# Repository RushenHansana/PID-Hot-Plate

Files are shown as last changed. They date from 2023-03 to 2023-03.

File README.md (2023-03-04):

# PID-Hot-Plate
This is the PID Hot Plate project we developed as the project for our Laboratory Practice module.
The contributors involved are Rushen Dissanayaka, Pabadhi Liyanage, Sithija Vihanga  and Oshan Yalegama.
The PCB designs and circuit schematics were created using Altium Designer.
The enclosure design was completed using Solidworks.

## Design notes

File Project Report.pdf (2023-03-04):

## University of Moratuwa Faculty of Engineering Department of Electronic & Telecommunication Engineering

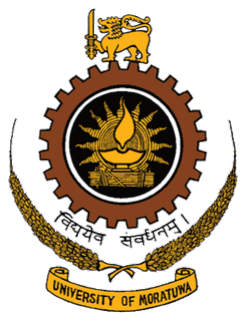
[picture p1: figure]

# Hot-plate Controller using PID

## Group Members(Group No. 24)

Index No. | Name
200134R 200352H 200506K 200740V | Disanayaka R.M.R.H. Liyanage P.H.S. Ranaraja S.V. Yalegama M.M.O.A.B.

## Submission Date: February 27, 2023

## This report is submitted as a partial fulfilment of module EN2091

## Contents

1 Introduction | 2
2 Functionality | 2
2.1 Sensor interfacing unit | | 2
2.2 PID controller unit | | 2
2.3 Firing Angle Unit | | 3
2.4 Power Supply Unit | | 3
2.5 Functional block diagram | | 4
3 System model with design parameters | 4
3.1 Sensor interfacing unit | | 4
3.2 PID controller unit | | 4
3.3 Firing angle unit | | 5
3.4 Power supply unit | | 5
4 Schematic | 5
4.1 Sensor interfacing unit | | 5
4.2 PID controller unit | | 5
4.3 Firing angle unit | | 5
4.4 Power supply unit | | 6
5 Simulation results | 6
5.1 PID controller unit | | 6
5.2 Sensor interfacing unit | | 6
5.3 Firing angle unit | | 6
5.4 PWM signal generation | | 7
5.5 Output | | 7
6 PCB design | 7
6.1 Sensor interfacing unit | | 7
6.2 PID controller unit | | 7
6.3 Firing angle unit | | 8
6.4 Power supply unit | | 8
7 Enclosure Design | 8
8 Individual contribution of each group member | 9
9 Conclusion and future works | 9

## Abstract

The objective of this project is to implement a hot plate controller using a PID controller unit. Here, we have used totally analog electronics-based concepts and a PID controller to keep temperature at a desired level. The implemented hot plate can be heated up to 200 ◦C. The PID controller takes the difference between the input temperature and the sensed temperature as the error signal, and then gives the sum of the proportional, derivative, and integral signals to the error signal as the output. Then, the firing angle controller unit controls the power by using PID output and keeps the temperature of the hotplate at the desired level.

## 1 Introduction

This is an analog electronics-based project. The primary concept which we have followed in this project is controlling the temperature of the hotplate by using a PID control unit. For the sake of ease and proper organization, the project has been divided into four main subtasks. The PID controller unit, sensor interfacing unit, firing angle, and power supply unit The difference between user input and sensor output is fed to the PID as an error signal. The PID controller generates proportional, derivative, and integral signals from the error signal. The firing angle unit generates a PWM signal according to the PID output to control the firing angle. Finally, from the power supply unit, a plate will be heated to the desired level. A specially designed hot plate can be heated up to 200 ◦C. As the hot plate’s input power supply, a 230-volt domestic power supply should be provided.

## 2 Functionality

### 2.1 Sensor interfacing unit

Measuring the current temperature of the coil is essential in order to control the temperature of the coil. Therefore, a temperature sensor is used to measure the current temperature. The sensor interface unit also takes the set temperature from the user as an input. It subtracts the voltage, which is calibrated according to the set temperature and the sensor output. Then, it generates the error signal. This error signal feeds the PID controller unit.

### 2.2 PID controller unit

PID is a feedback-based control strategy that adjusts the system’s output based on the difference between the desired setpoint and the actual variable. Instrument Society of America[1].The proportional term provides an output signal that is proportional to the error signal that is given by the sensor interface unit. The integral term sums up the error over time and produces an output to reduce any steady-state error. This aids in reaching the hot plate at the precise temperature set by the user. The derivative term measures the rate of change of the error and produces a control output to decrease overshoot. With the optimal combination of these three terms, we can reduce the time taken to reach the set temperature and maintain it exactly at the required level.
The proportionality constant is represented by the letter ”Kp” and determines the proportion of the error signal that is applied to the control output. Increasing Kp will increase the responsiveness of the system. However, it can also lead to overshoot and instability.
The integral constant, represented by the letter ”Ki,” determines the amount of past error that is summed up and used to adjust the control output. This term involves reducing steady-state error. But it can also lead to instability if the value of ”Ki” is too high.
The derivative constant, represented by the letter ”Kd,” determines the rate at which the error is changing over time and uses this information to adjust the control output. This term helps to reduce overshoot. The optimal values of these constants are achieved by a process called tuning.
The sum of proportional, integral, and derivative signals will be fed to the firing angle unit

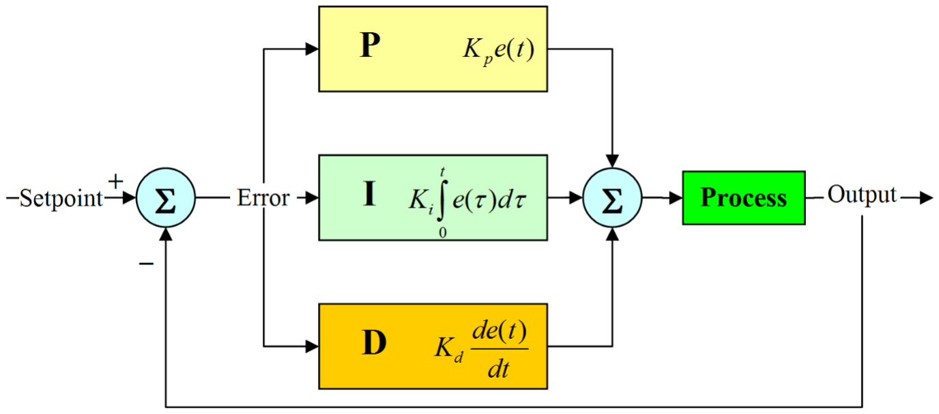
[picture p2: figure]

Figure 1: functionality diagram of a PID controller

### 2.3 Firing Angle Unit

Introduction

The firing angle unit controls the amount of power supplied to the coil based on PID output. Zero crossing detection, ramp generation, PWM signal generation, and the TRIAC control circuit are the main subunits of the firing angle unit.

1. Detection of Zero Crossings
In order to detect zero-crossings, each halfcycle of the AC waveform is given an equal pulse. This enables control of every halfcycle of the AC waveform in the same way. When the voltage of the rectified AC waveform is lower than 0.7V, the output of the zero-crossing detector is 12V; it is zero otherwise.

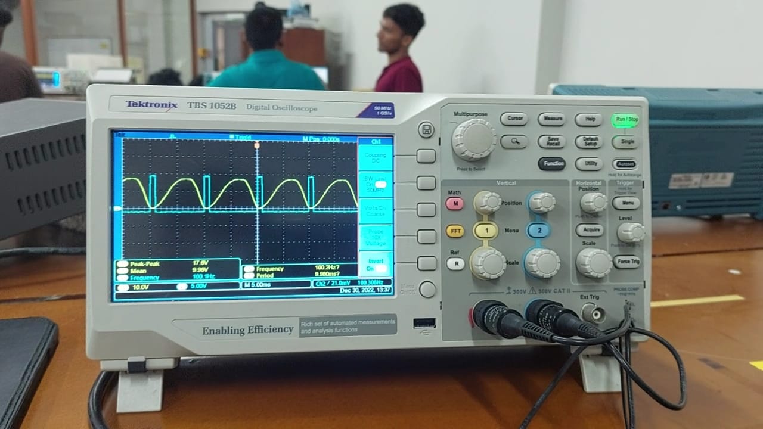
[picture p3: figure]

2. Ramp Generation
The ramp is generated by charging and discharging a capacitor. When the output of the zero-crossing detector is less than the threshold voltage of the transistor, the capacitor will be charged. When the output of the zero-crossing detector is high, the transistor will be saturated and the capacitor will be discharged. The ramp works as a threshold for PWM signal generation.

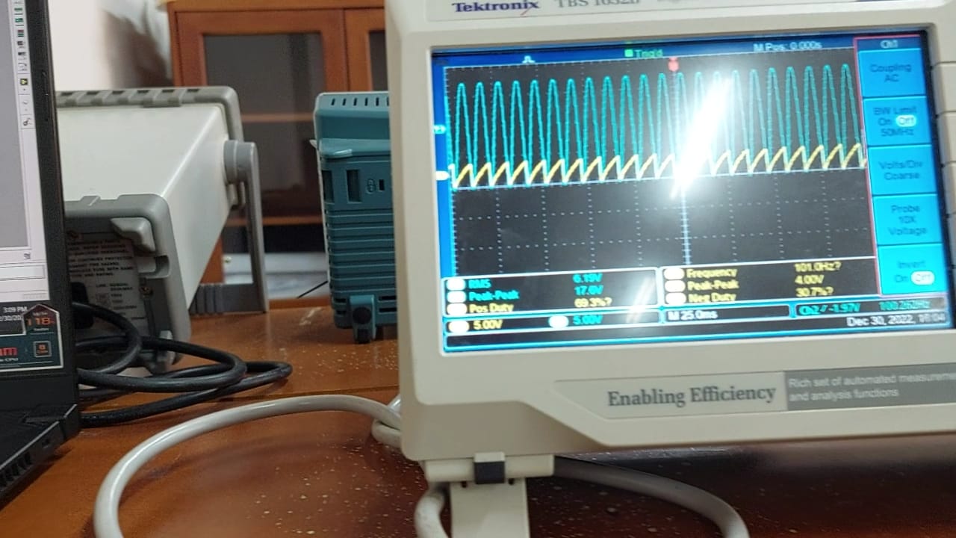
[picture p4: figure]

3. PWM signal generation
The main task of this subunit is to create a PWM signal, which is used to control the AC power. When the ramp voltage is lower than the PID output voltage, the output of the subunit is 0V and otherwise, it is 12V. The width of the pulse gradually decreases when the output voltage of the PID increases. Conversely, pulse width increases when the output of the PID drops.

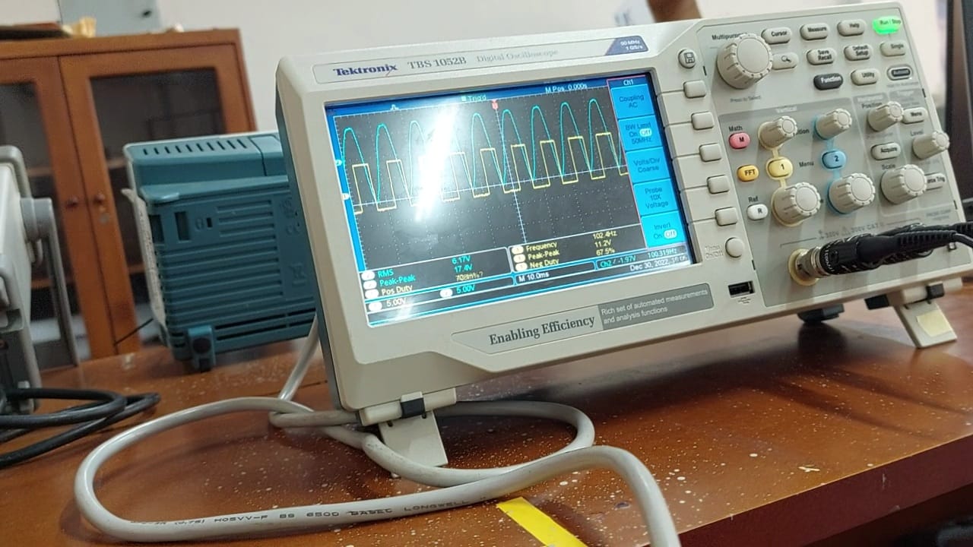
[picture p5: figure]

4. TRIAC Control Circuit
The PWM signal is passed to the optocoupler through a transistor. The optocoupler creates electrical isolation between the lowand high-voltage circuits. The TRIAC, which is connected to the optocoupler, acts as a switch to the AC source. The optocoupler’s output signal, which is connected to the TRIAC, controls the AC waveform.

### 2.4 Power Supply Unit

The hotplate draws power from the domestic power supply (230 V, 50 Hz). But the sensors, opamps, and most of the other components use low voltage to function. For instance, op-amps function at -12V and 12V. The function of the power supply unit is to supply the required voltages to relevant components.

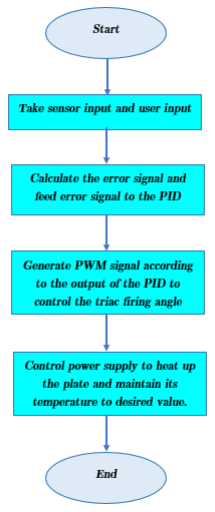
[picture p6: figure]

### 2.5 Functional block diagram

## 3 System model with design parameters

### 3.1 Sensor interfacing unit

There are several options available in sensing the temperature of the hot plate. When deciding a sensor to be used, the requirements that should be fulfilled by the sensor are, a linear relationship between voltage and temperature, compactness, high operating temperature, availability in the market, quick response time and simplicity in signal processing. One of the available options is a thermocouple but it is not suitable for our project due to the need for a reference temperature and the complexity of the signal processing required. We decided to use a PT100 which is an RTD (Resistance Temperature Detector). The sensor has an operating temperature of up to 800C and has a resistance that varies with temperature. The sensor interface produces an output voltage corresponding to the resistance of the sensor by the

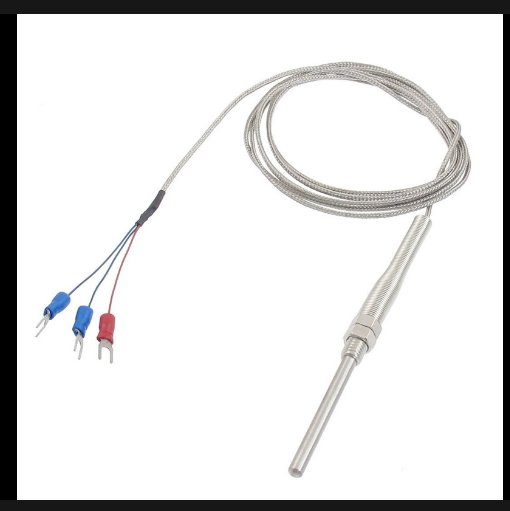
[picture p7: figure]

use of a constant current built from a BJT and amplifies and calibrates the result. The resulting voltage is then passed through a subtractor which calculates the error signal between this voltage and the voltage corresponding to the temperature set by the user. The resulting error signal is passed to the PID.
UA741 Op-amps were used throughout the interface as they perform well as voltage followers.
(a) PT100 sensor

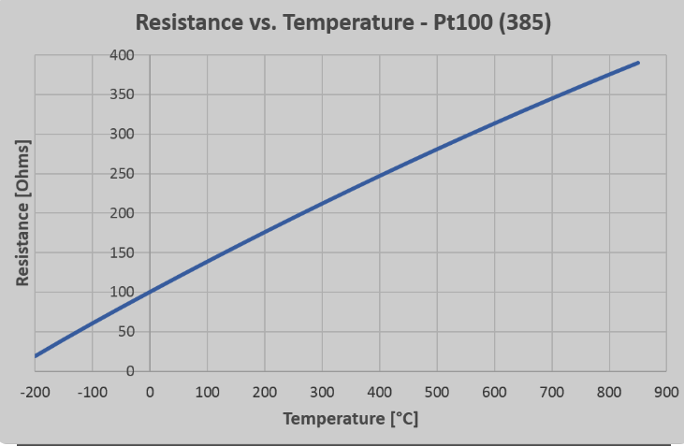
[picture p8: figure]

(b) Relationship between resistance vs temperature

Figure 2: For 100 kHz

Required temperature (input temperature by the user) and the current temperature are displayed by the OLED display.

### 3.2 PID controller unit

PID controller unit consist with an inverting amplifier, integrator circuit, subtractor circuit and a scaling adder. UA741CP op-amps are used to build those circuits due to its high gain, low input bias current, low input offset voltage and low cost. In each inverting amplifier, subtractor and integrator circuits, a pre-set is used as a feedback resistor and by changing the resistor value of the three pre-sets, Kp, Ki and Kd values can be changed.

### 3.3 Firing angle unit

We’re using LM324n op-amps for the triac firing angle circuit because they have enough slew rate to charge and discharge the 50V, 10uF capacitor with the generated impulse function (which is generated by comparing the full wave rectified 30V signal with 0.7V of the diode). For all the op-amps, we have used 12V and 0V as the power supply because we need to get a PWM signal as a positive output. For calibration purposes, two pre-sets have been added to user input voltage and to control the PWM signal amplitude. Because of that, a triac circuit can be independent from other input and output circuits. To handle both the 12V DC supply and the high-power supply for the load, we are using the optocoupler MOC3021, which can function up to 400V high power voltage. Moreover, triac BT137 has been used to slice the output AC supply voltage with respect to the input PWM signal to the optocoupler. On the high-power side, the triac can operate at up to 600 volts.

### 3.4 Power supply unit

The power supply unit consists of a center-tapped transformer, a rectifier bridge, capacitors, and voltage regulators. A center-tapped transformer converts domestic voltage into 12 volts. To obtain full wave rectification of the AC signal, a rectifier bridge is used. Unnecessary noises are avoided by the capacitors.

## 4 Schematic

### 4.1 Sensor interfacing unit

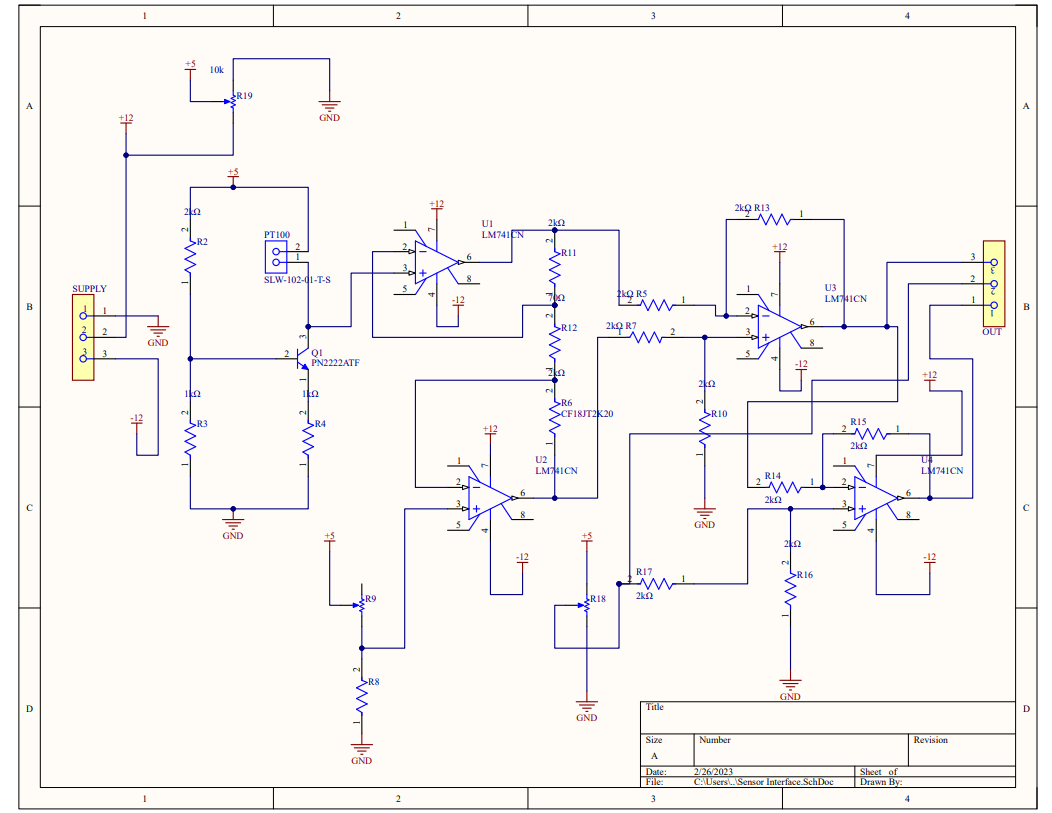
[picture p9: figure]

### 4.2 PID controller unit

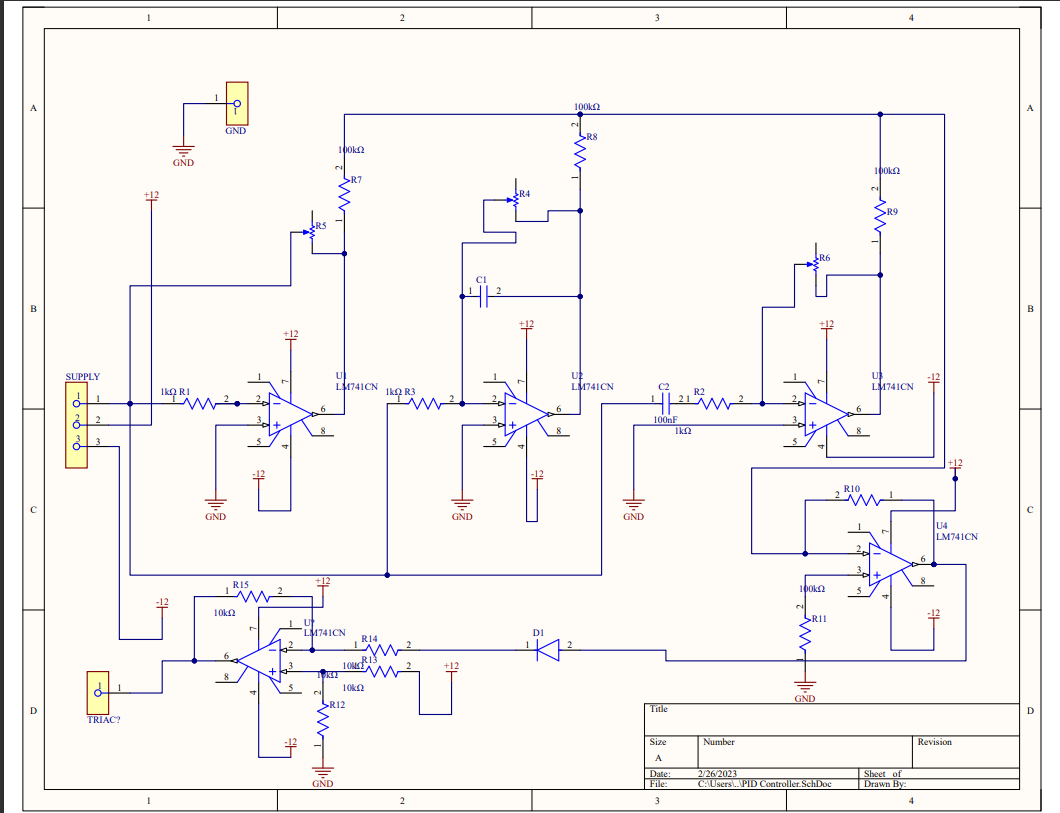
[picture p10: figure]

### 4.3 Firing angle unit

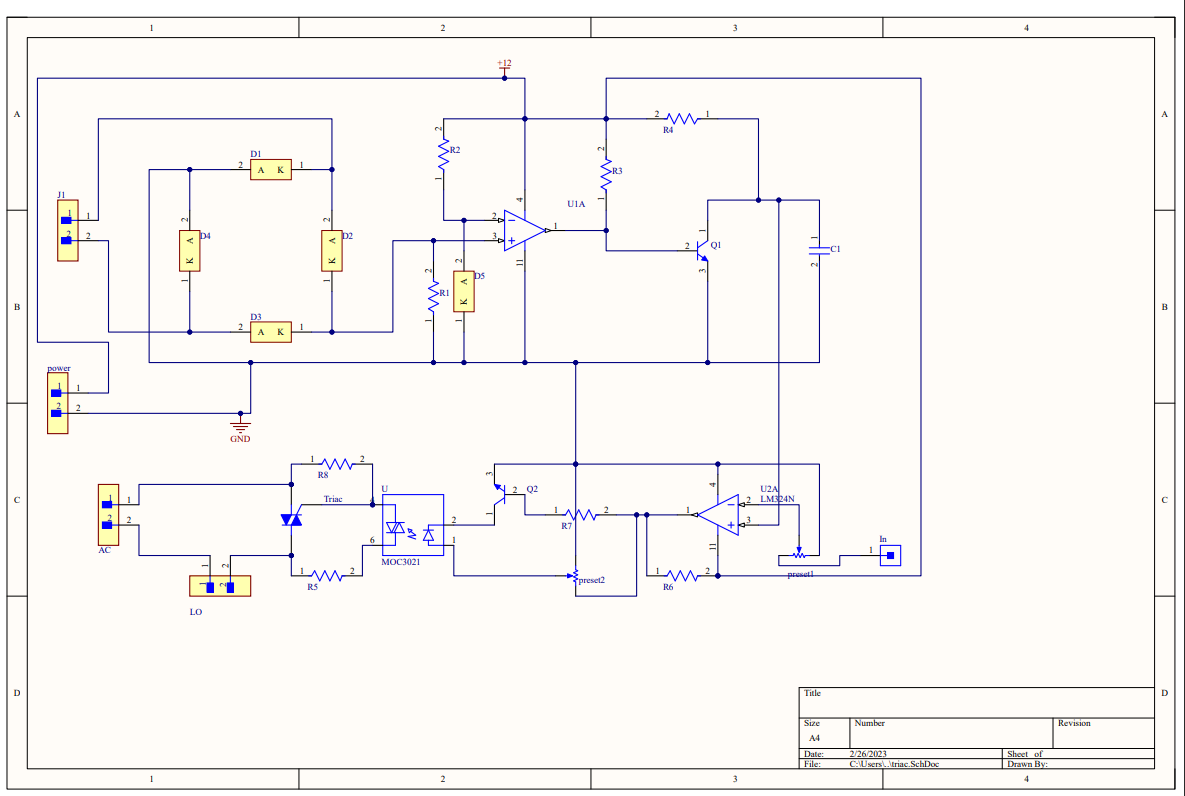
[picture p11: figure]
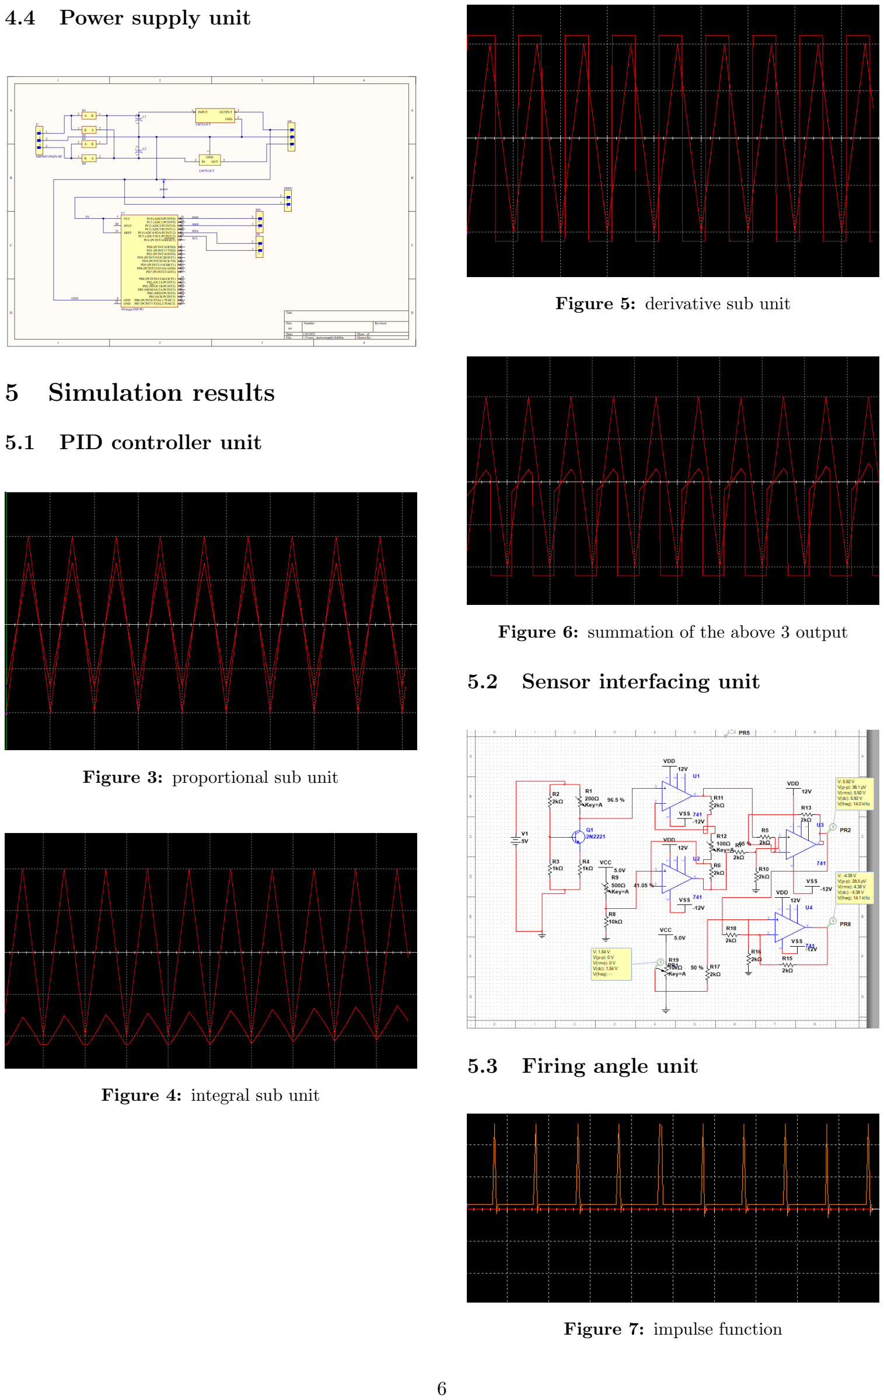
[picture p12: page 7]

### 4.4 Power supply unit

## 5 Simulation results

### 5.1 PID controller unit

Figure 3: proportional sub unit

Figure 4: integral sub unit

Figure 5: derivative sub unit

Figure 6: summation of the above 3 output

### 5.2 Sensor interfacing unit

### 5.3 Firing angle unit

Figure 7: impulse function

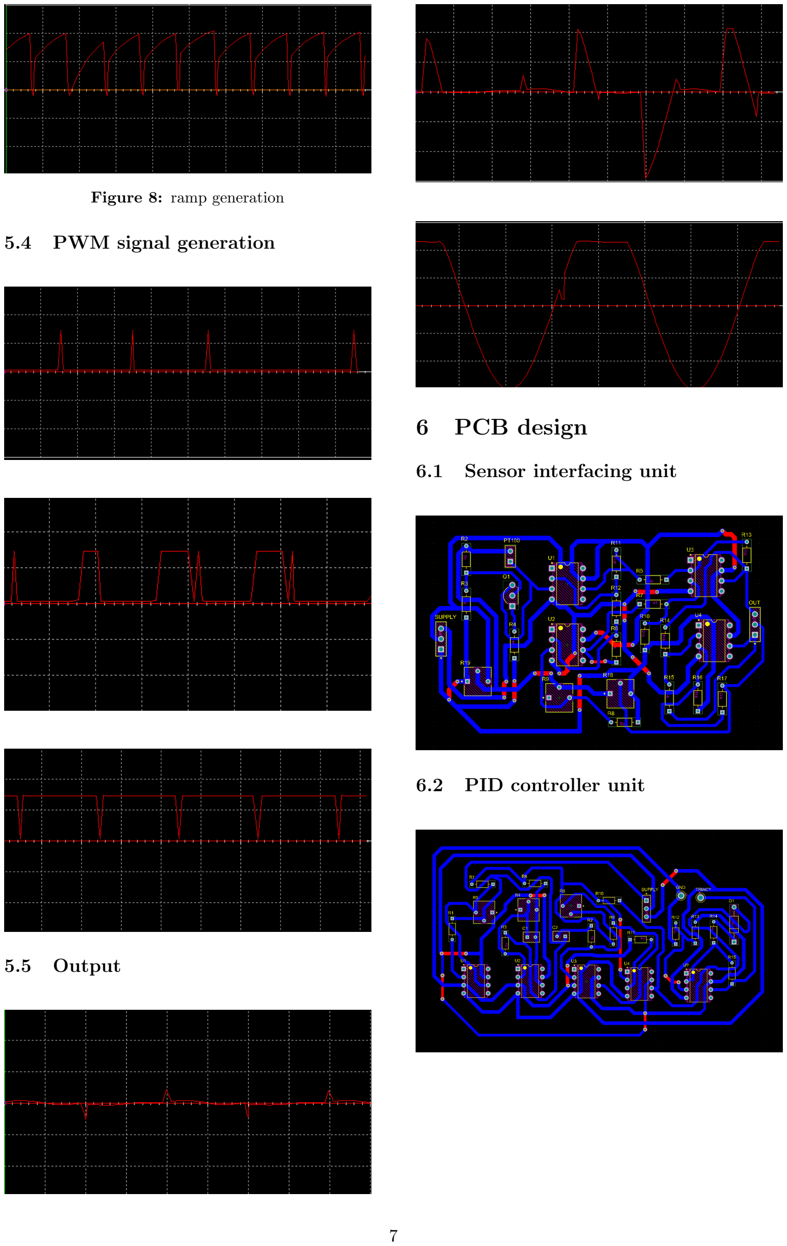
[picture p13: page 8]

Figure 8: ramp generation

### 5.4 PWM signal generation

### 5.5 Output

## 6 PCB design

### 6.1 Sensor interfacing unit

### 6.2 PID controller unit

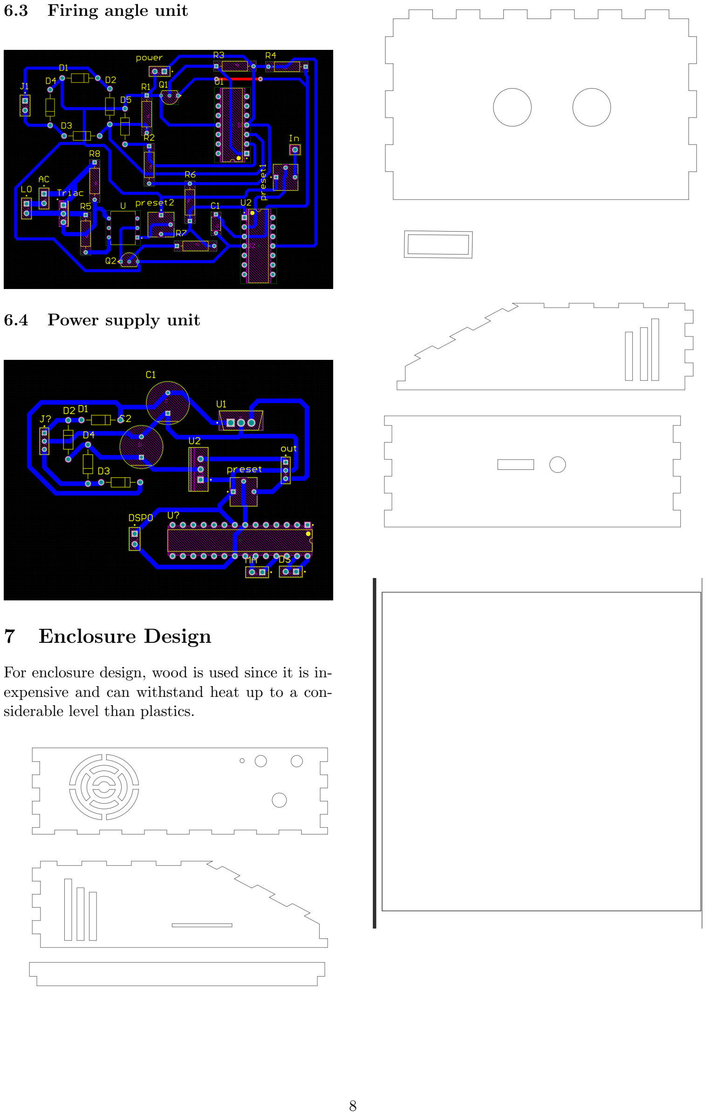
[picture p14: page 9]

### 6.3 Firing angle unit

### 6.4 Power supply unit

## 7 Enclosure Design

For enclosure design, wood is used since it is inexpensive and can withstand heat up to a considerable level than plastics.

## 8 Individual contribution of each group member

Group Members

Name. | Contribution
Disanayaka R.M.R.H. (200134R) | Power supply unit design
Liyanage P.H.S. (200352H) | PID control unit design
Ranaraja S.V. (200506K) | Firing angle unit design
Yalegama M.M.O.A.B. (200740V) | Sensor interfacing unit design

## 9 Conclusion and future works

In conclusion, the hot plate has been implemented by interconnecting four sub units which are sensor interfacing unit, PID controller unit, Firing angle unit and the power supply unit. The hotplate can be heated up to 200 ◦C. Also, the user can easily get the required information that he needs from the OLED display.
We are hoping to improve our hotplate design further in future. For that, we expect to tune the PID controller circuit precisely to get the optimal Kp, Ki and Kd values.
From those optimal values, we can heat up the coil up to desired temperature more quickly and maintain the hotplate temperature exactly at the desired temperature./

## References

[1] Karl J Astrom. “PID controllers: theory, design, and tuning”. In: The International Society of Measurement and Control (1995).

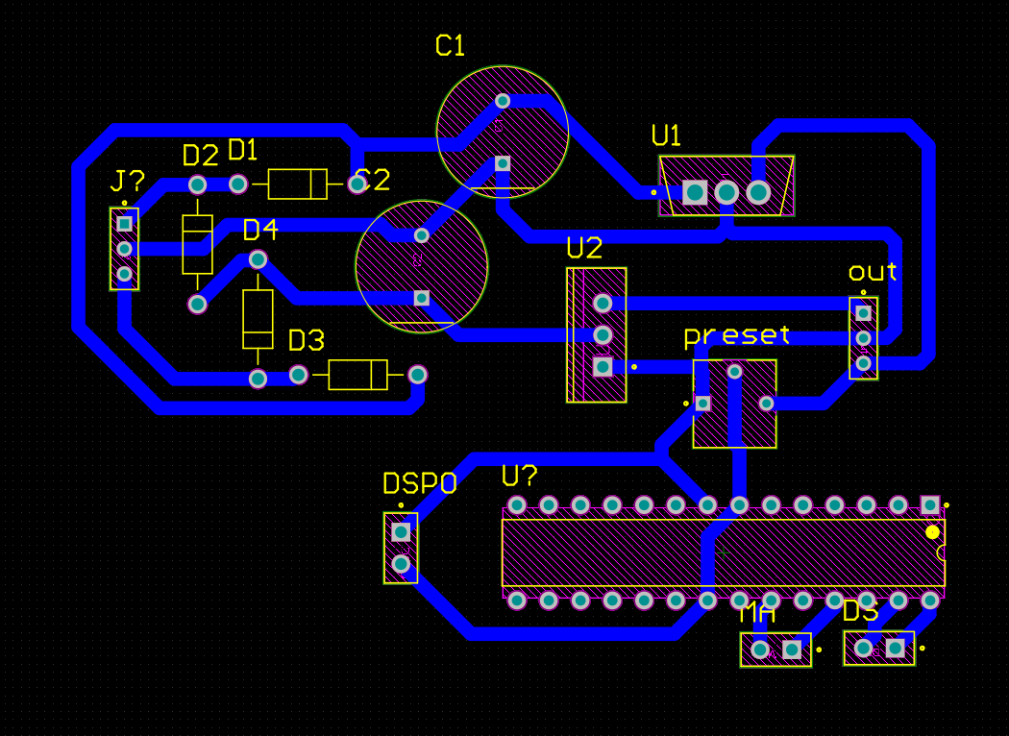
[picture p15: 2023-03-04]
Report files/pcbs/powersupply.png

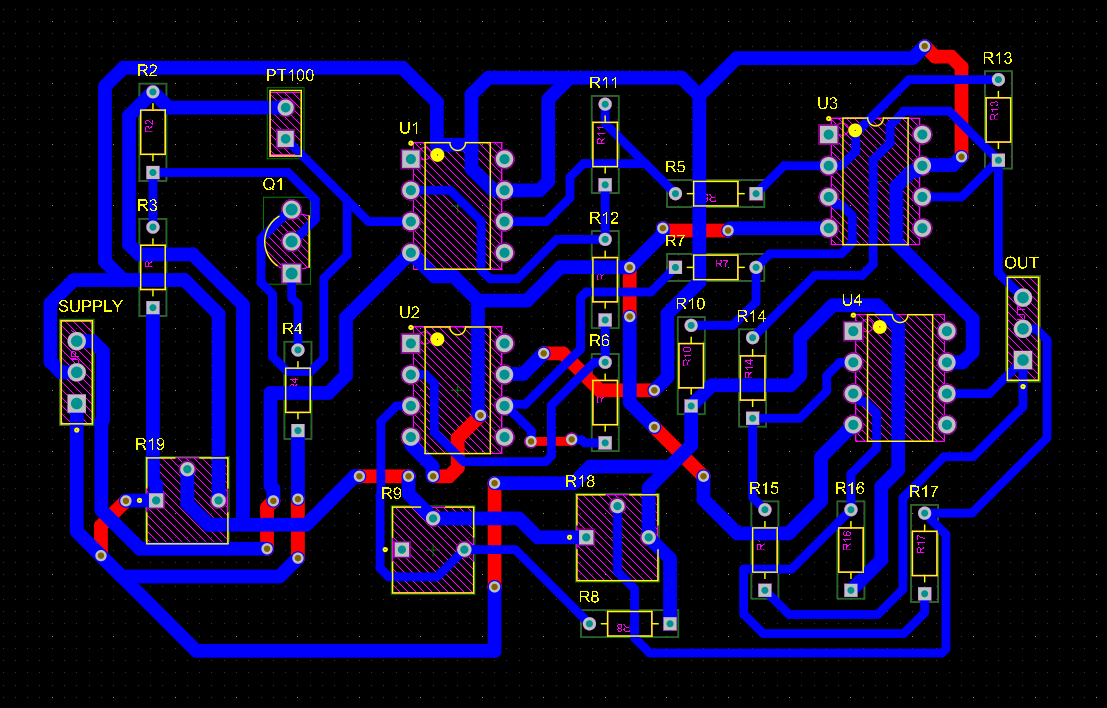
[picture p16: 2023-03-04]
Report files/pcbs/Sensor Interface.png

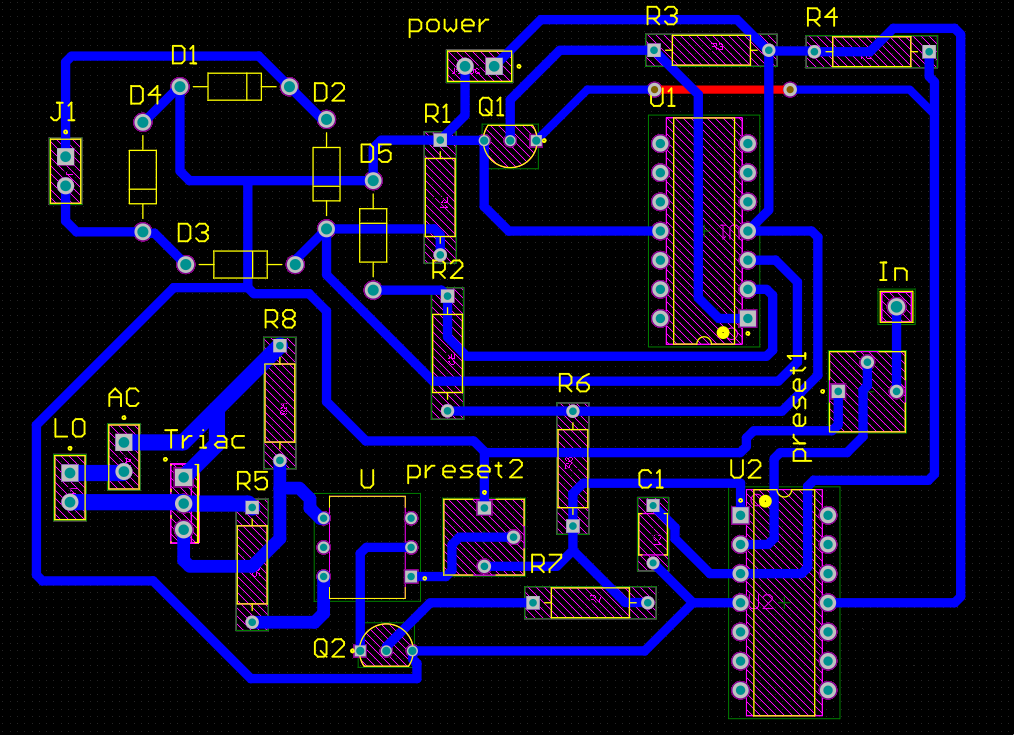
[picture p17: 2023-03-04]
Report files/pcbs/triac.png

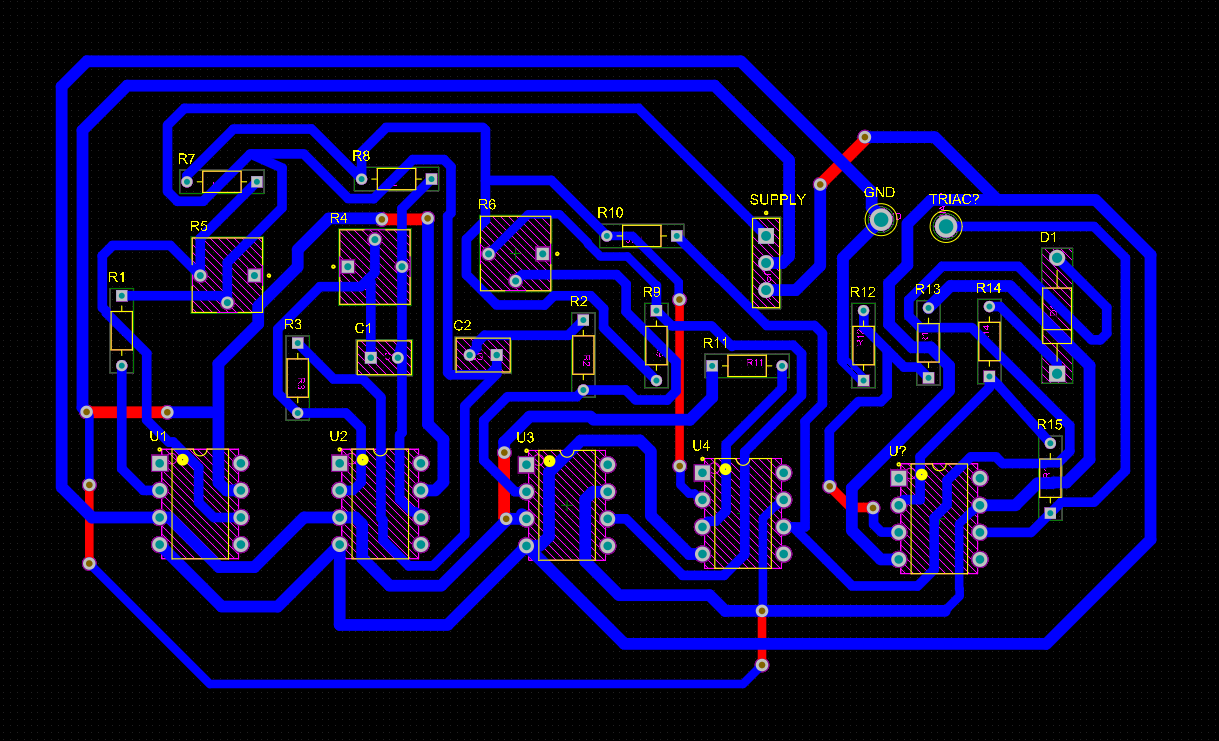
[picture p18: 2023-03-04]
Report files/pcbs/PID controller.png

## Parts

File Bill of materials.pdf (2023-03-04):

Item | Quantity | Price per each | Price
230V to 12V stepdown transformer (20:1) x 1 | 1 | 210 | 210
1B4B42 | 2 | 50 | 50
capcacitors 2.2 micro F | 2 | 10 | 20
Variable resistors 1k ohm | 1 | 50 | 50
LM324ADG | 3 | 50 | 150
1N4007G | 3 | 15 | 45
2N2222A | 5 | 10 | 50
Variable resistors 10k ohm | 1 | 50 | 50
Optocoupler MOC3021 | 2 | 60 | 60
2N5568 | 3 | 15 | 45
Resistors 100 ohm | 20 | 2.5 | 50
Capacitors
100nF 600V | 1 | 50 | 50
100nF 400V | 1 | 50 | 50
Variable resistor 500K | 1 | 80 | 80
Opamp LM741 CN | 6 | 20 | 120
1k ohm | 20 | 2.5 | 50
100k ohm | 20 | 2.5 | 50
Potentiometer
20k ohm | 2 | 80 | 160
100k ohm | 2 | 80 | 160
diode | 2 | 15 | 30
capacitors 0.1 micro F | 2 | 50 | 50
ATMega 328p | 1 | 1500 | 1500
OLED | 1 | 900 | 900
PT100 | 1 | 260 | 260
Heating coil | 1 | 710 | 710
PCB designing | | | 2110
Enclosure | | | 2000
Total cost | | | 9060

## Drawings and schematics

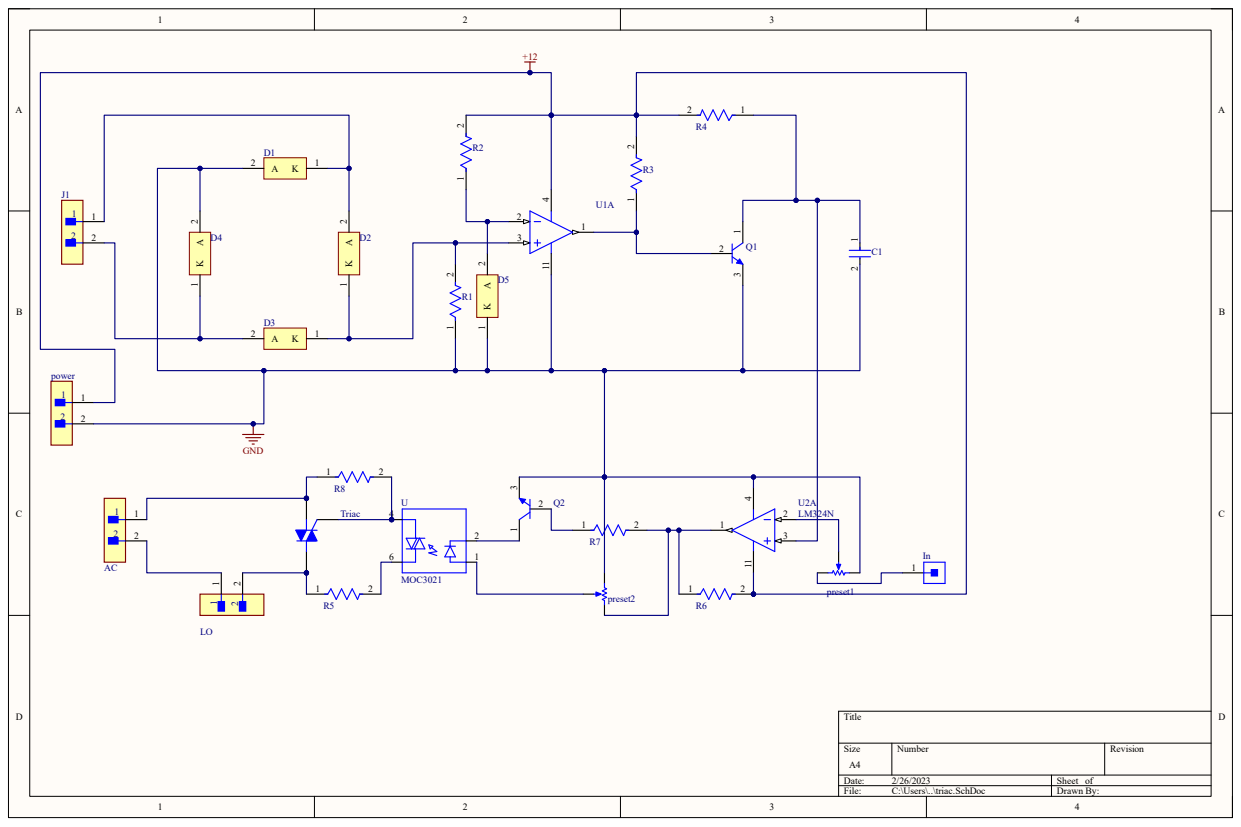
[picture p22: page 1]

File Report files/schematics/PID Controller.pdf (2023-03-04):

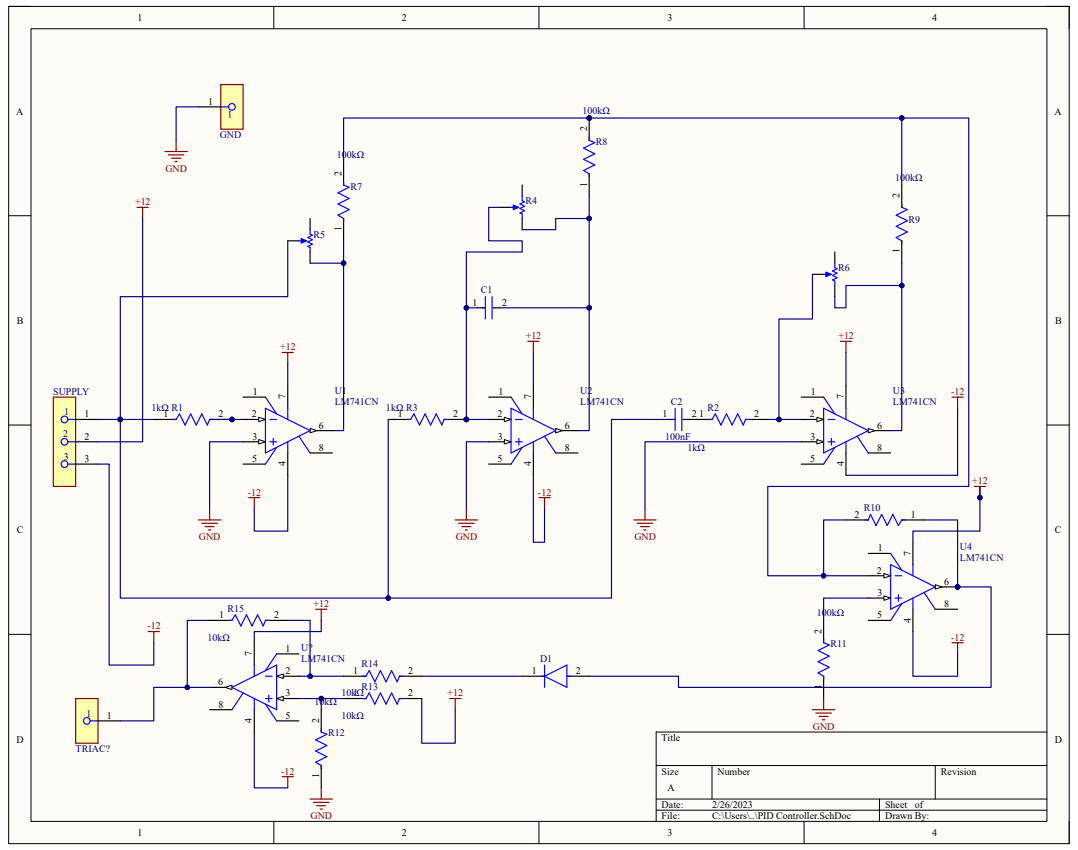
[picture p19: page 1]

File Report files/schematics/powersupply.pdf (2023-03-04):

+ C1 1 2

# out 12 12

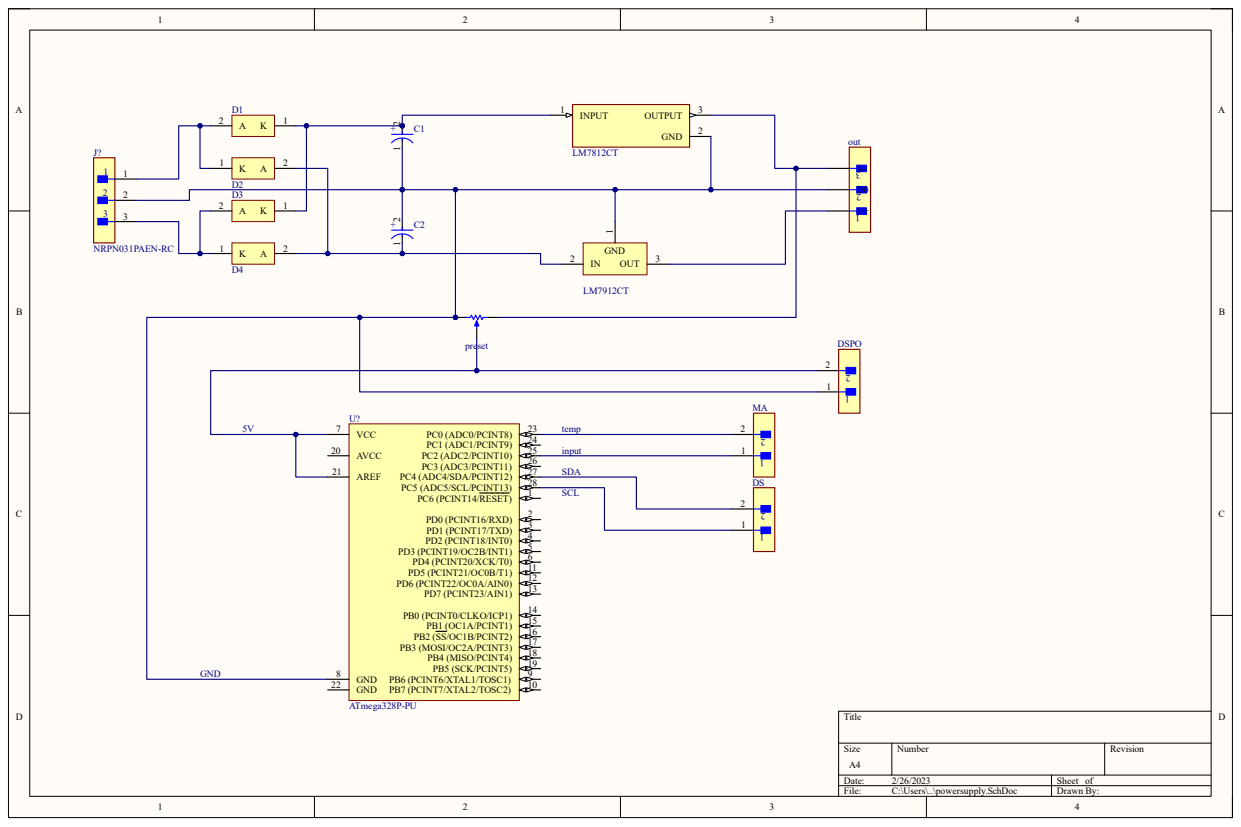
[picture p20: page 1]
Title; Size; Number; Revision; Date:; Sheet of; File:; C:\Users\..\powersupply.SchDoc; Drawn By:; PC6 (PCINT14/RESET); PD0 (PCINT16/RXD); PD1 (PCINT17/TXD); PD2 (PCINT18/INT0); PD3 (PCINT19/OC2B/INT1); PD4 (PCINT20/XCK/T0); VCC; GND; 8 PB6 (PCINT6/XTAL1/TOSC1); PB7 (PCINT7/XTAL2/TOSC2); PD5 (PCINT21/OC0B/T1); PD6 (PCINT22/OC0A/AIN0); PD7 (PCINT23/AIN1); PB0 (PCINT0/CLKO/ICP1); PB1 (OC1A/PCINT1); PB2 (SS/OC1B/PCINT2); PB3 (MOSI/OC2A/PCINT3); PB4 (MISO/PCINT4); PB5 (SCK/PCINT5); AVCC 20; AREF 21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

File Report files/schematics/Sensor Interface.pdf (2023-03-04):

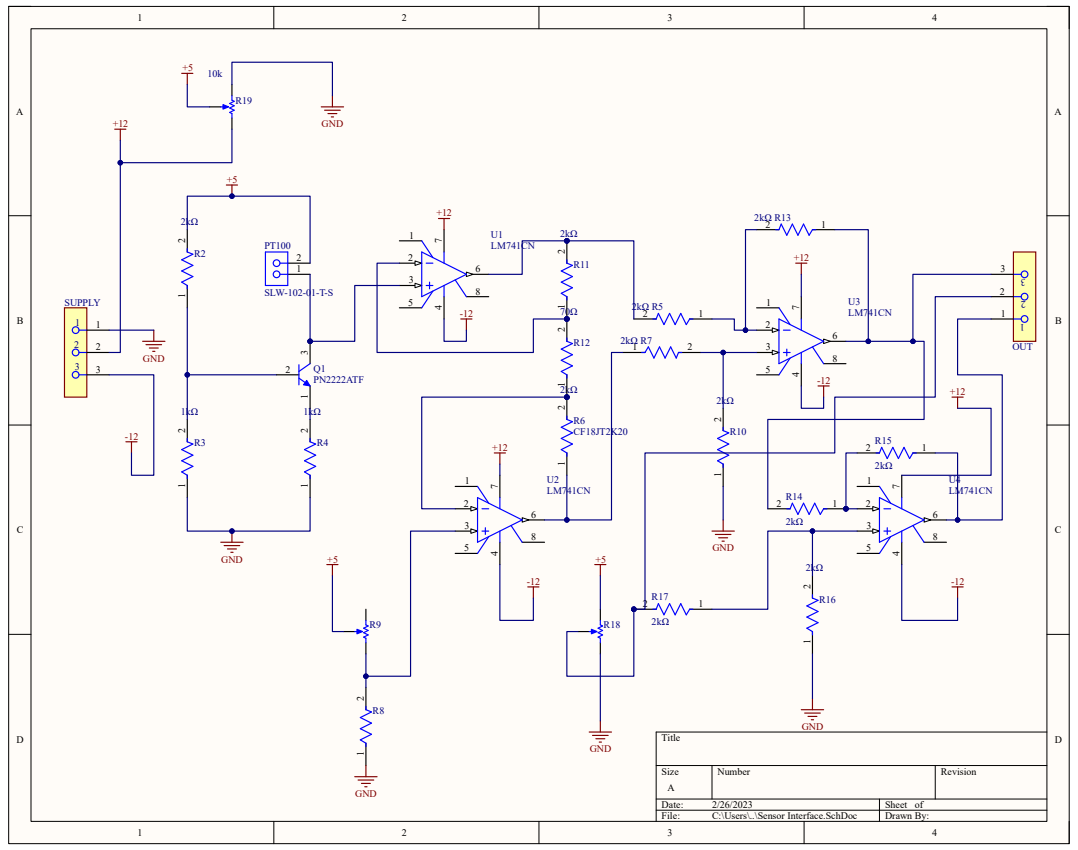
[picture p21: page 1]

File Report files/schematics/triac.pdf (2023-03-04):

## R1¹ ²
